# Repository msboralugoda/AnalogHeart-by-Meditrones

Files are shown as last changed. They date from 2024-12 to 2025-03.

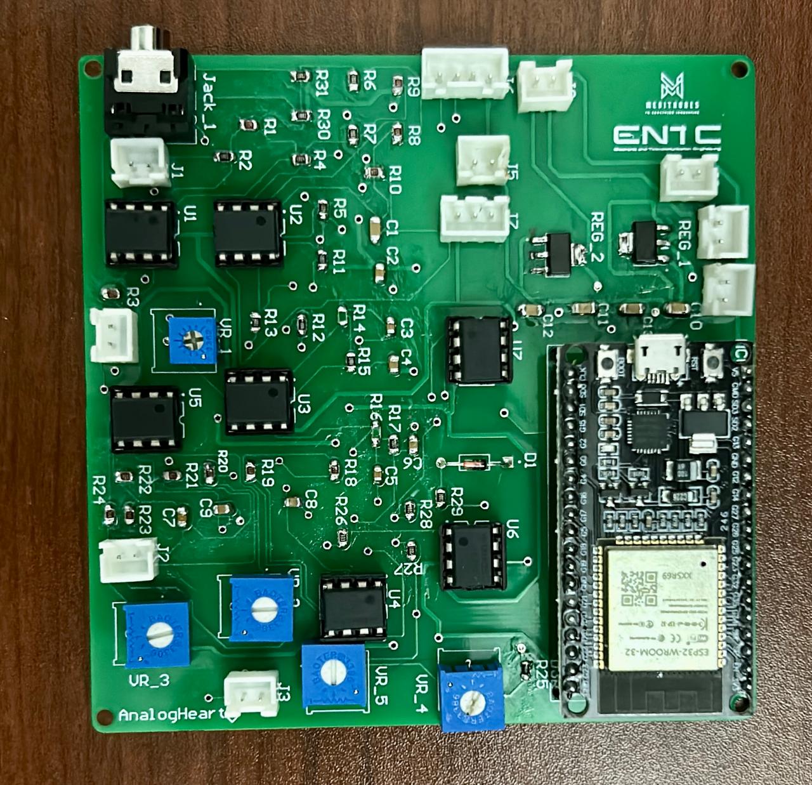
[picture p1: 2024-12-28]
Media/soldered pcb.jpg

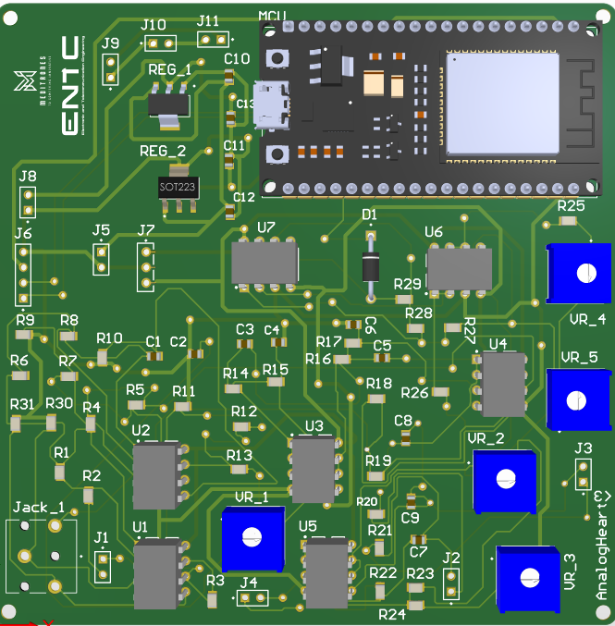
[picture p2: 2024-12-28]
Media/3D.png

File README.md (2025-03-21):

# AnalogHeart-by-Meditrones
This is the detailed project description of the ECG monitoring device built using analog electronics by the team Meditrones.
## Table of Contents
1. [Introduction](#introduction)
2. [Functionality](#functionality)
3. [Printed Circuit Board](#printed-circuit-board)
4. [Enclosure Design](#enclosure-design)
5. [Contributors](#contributors)

---

## Introduction
An electrocardiogram (ECG) is a widely used diagnostic tool for evaluating heart activity by detecting electrical signals through electrodes attached to the skin. These signals have amplitudes ranging from 0.001 mV to 100 mV and frequencies between 0.01 Hz and 180 Hz. However, amplifying and filtering these signals presents challenges due to their susceptibility to noise, power line interference, and other distortions.

Our project aims to address these challenges by designing an analog circuit that amplifies and filters ECG signals using basic electronic components such as resistors, capacitors, and operational amplifiers (OpAmps). The design incorporates multiple stages of signal conditioning, which are detailed below.

We simulated the design using LTSpice before implementation and used Altium Designer for PCB layout and SolidWorks for enclosure design.
Simulated Circuit

---

## Functionality
The AnalogHeart ECG Monitor includes the following features:
- **Real-time heart rate monitoring.**
- **User-friendly interface for operation.**
- **Accurate heart rate display with filtering.**
- **Adjustable settings for different scenarios.**
- **Data logging and export options.**
- **Detailed documentation for developers and users.**

### Signal Conditioning Stages
1. **Instrumentation Amplifier**
   - Amplifies small differential signals from the electrodes while rejecting common-mode noise.
   - Implemented using TL072CP OpAmps for high Common Mode Rejection Ratio (CMRR).
   - Adjustable gain using an external potentiometer.

2. **Right Leg Drive**
   - Reduces common-mode noise by injecting an inverted signal back into the body.
   - Built using a TL072CP OpAmp configured as an inverting buffer.

3. **Filter Stages**
   - **High Pass Filter**: Removes low-frequency noise and DC offset. First-order design with a cutoff at 0.15 Hz.
   - **Low Pass Filter**: Eliminates high-frequency noise using a fifth-order Bessel filter with a cutoff at 164 Hz.
   - **Notch Filter**: Suppresses power-line interference (50/60 Hz) with a Twin-T configuration and adjustable parameters.

4. **Power Circuit**
   - Dual supply (+12V and -12V) generated by TPS61040 boost converters for OpAmps.
   - 3.3V regulated output for ESP32 MCU using AMS117-3.3 regulator.
   - Rechargeable Li-Po battery support with a charging module for portability.

5. **Analog-to-Digital Conversion**
   - Captures conditioned ECG signals via ESP32's ADC input.
   - Includes level-shifting and scaling circuits to ensure signals fit within the 0-3.3V input range of the ESP32.

---

## Printed Circuit Board
The PCB was designed using Altium Designer and features:
- **Two-layer layout** for signal integrity and minimal interference.
- **Separate routing** for signal and power traces to reduce noise.
- **Compact design** with 0805 SMD components and IC bases for easy replacement.
- **Hand-soldered components** for prototyping and testing.
PCB

### PCB Highlights:
- **Power traces**: 25 mils for reliability.
- **Signal traces**: 15 mils to maintain integrity.
- **Isolated signal processing**, power, and ADC circuits.

---

## Enclosure Design
The enclosure was modeled using SolidWorks and designed for:
- **Protection and ventilation** to prevent overheating.
- **Removable top lid** for easy assembly and maintenance.
- **Battery holder and charging port** for portability.
- **Display mount and slots** for connectors, switches, and ventilation.
- **3D-printed construction** for rapid prototyping.


---

## Contributors
- **Aazir M.M.M** - Circuit design, enclosure design, and optimization.
- **Boralugoda M.S** - PCB design, documentation, and testing.
- **Liyanage D.L.B.B** - Circuit design, PCB assembly, and soldering.
- **Madusanka S.P.S** - Enclosure design and circuit testing.

---

For further details, visit the GitHub repository: [AnalogHeart by Meditrones](https://github.com/Banu-Liyanage/AnalogHeart-by-Meditrones)

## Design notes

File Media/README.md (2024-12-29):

This contain all the results and final design outputs of the project 
product_analog
This is the final device with the electrodes connected to the device.

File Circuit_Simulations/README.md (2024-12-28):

This contains the pathway to the circuit development and testing which includes the schematics and simulated results.
ECG_circuit_diagram
Above shown circuit is the main circuitry of the analog heart ecg monitoring device and it mainly consists of the Instrumentational Amplifier, High Pass Filter, Low Pass Filter and the Notch Filter

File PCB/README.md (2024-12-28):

This includes the PCB schematics of the analog project by team meditrones about the heart ECG monitoring device.

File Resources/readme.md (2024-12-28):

This contains some important resources we used while developing the circuit and for debugging purpoese as well.

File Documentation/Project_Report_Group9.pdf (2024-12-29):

Department of Electronic and Telecommunication Engineering

University of Moratuwa

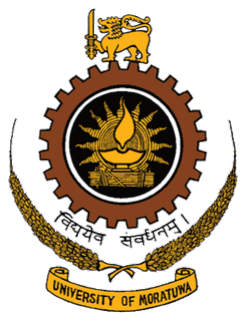
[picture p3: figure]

# AnalogHeart ECG Monitor

## Team Meditrones

## EN2091 - Laboratory Practice and Projects

Aazir.M.M.M - 220005R
Boralugoda.M.S - 220074B
Liyanage.D.L.B.B - 220362G Madusanka.S.P.S - 220374U

# Contents

1. | Introduction | | 2
2. | Functionality | | 3
2.1. | Instrumentation Amplifier | | | 3
2.2. | Right Leg Drive | | 3
2.3. | Filter Designing | | 3
2.4. | High Pass Filter | | 4
2.5. | Low Pass Filter | | 4
2.6. | Notch Filter | | 4
2.7. | Power Circuit | | 5
2.8. | Analog to Digital Conversion circuit | | 5
3. | Design Parameters | | 5
3.1. | Instrumentation Amplifier | | 5
3.2. | High Pass Filter | | 5
3.3. | Low Pass Filter | | 5
3.4. | Notch Filter | | 6
4. | PCB Design | | 6
5. | Enclosure Design | | 6
6. | Simulations and test Results | | 6
7. | Final Prototype | | 6
8. | Task Allocation | | 7
9. | Resources | | 7
10. References | | 7
11. Appendix | | 9
11.1. | PCB Layout from Altium Designer | | 9
11.2. Enclsoure Design using Solidworks | 10
11.3. Circuit Simulation and results | 12
11.4. Circuit Testing | 12

1

## Abstract

Our project was to create a circuitry that is capable of apprehending the ECG waveform and displaying it.This was achieved only using analog electronic components and they were used for several stages such as amplification, filtering and sampling purposes. Circuit is mainly made of instrumentation Amplifier , High Pass Filter,Low Pass Filter and a Notch Filter. This report also includes the PCB designs, simulations and the 3D Enclosure design made to meet the project requirements.

## 1. Introduction

An electrocardiogram (ECG) is a straightforward diagnostic method used to evaluate the electrical activity of the heart by identifying electrical impulses produced by electrodes affixed to the skin during each heartbeat. By using a feedback mechanism through the right leg, the voltage differential between the left and right arms is amplified. These voltages from the right arm, left arm, and right leg are measured via ECG leads. The voltage signal has a frequency between 0.01 Hz and 180 Hz and an amplitude between 0.001 mV and 100 mV (usually 1 mV).
The limited amplitude of the raw ECG signals and their vulnerability to distortion from a variety of causes, including noise, power line interference, radiofrequency interference, noise from electrode contact, stray capacitance and other biological factors makes it difficult to amplify and filter the ECG signal. Our circuit is composed of analog components like resistors, capacitors and OpAmps that is capable of amplifying and filtering out the ECG signal. Our circuit comprises of the following sections;
- Instrumentation Amplifier
- First Order Active High Pass Filter
- Fifth Order Active Low Pass Filter
- Notch Filter
- Right Leg Drive

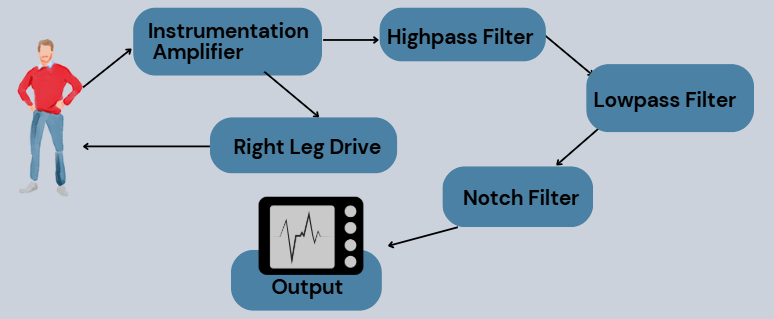
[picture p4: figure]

Figure 1: Functional block diagram

After simulating the circuit using LT-Spice we successfully implemented the prototype circuit and designed a PCB using Altium as well as an enclosure to meet the user demands using Solidworks.

2

## 2. Functionality

### 2.1. Instrumentation Ampli-

fier

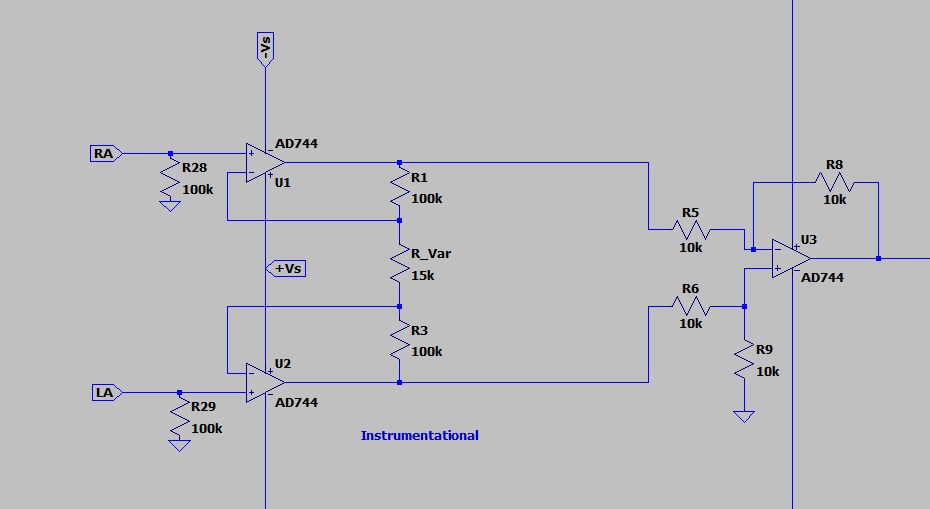
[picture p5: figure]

Figure 2: Instrumentation Amplifier

The main purpose of the instrumentation amplifier is to amplify the small electrical signals produced by the heart, which are typically in the millivolt range. It achieves this by amplifying the differential voltage between two electrodes while suppressing common-mode signals, such as interference from nearby power lines or artifacts from other biosignals.

In our instrumentation amplifier circuit design, it utilizes two
TL072CP | operational | amplifiers.
This IC was chosen for its moderate Common Mode Rejection Ratio (CMRR), with a value of 80 dB, making it sufficient for the amplification process. The circuit receives input through two ECG leads placed near Right and Left collarbones, and the gain can be adjusted using a variable resistor located centrally.

### 2.2. Right Leg Drive

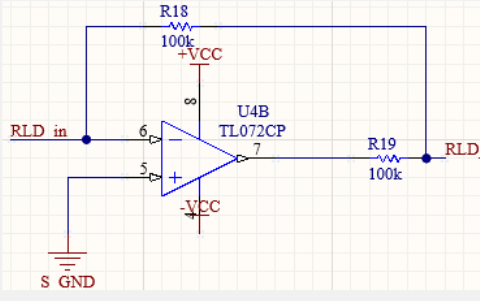
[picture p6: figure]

Figure 3: Right Leg Drive

The Right Leg Drive (RLD) circuit is used to reduce the common-mode noise between the two input electrodes. This is achieved by getting the original signal, inverting and amplifying it, then sending it back to the body through an electrode placed below the ribs. Here we use a single TL072CP IC and it acts as an inverting unity gain buffer.

### 2.3. Filter Designing

Selection of the proper cut off frequencies and the orders of the filters were few key things we had to consider when designing the circuit, by the literature review we did we came to a conclusion that the bandwidth of 160 Hz would be ideal and achievable from the available resources.The filter circuit consists of 1st Order High Pass Filter, 5th Low Pass Bessel Filter and a Twin-T Notch Filter.We decided to use TL072CP OpAmps for our filter circuits due to its better performance under noise.

3

### 2.4. High Pass Filter

Used to remove low-frequency noise and the DC offset from the ECG signal, such as baseline wander caused by patient movement or breathing. We decided to use a first order High Pass Filter because its performance met our expectations and we didn’t want to make the circuit bulky and costly by increasing order of the filter, the cut off frequency of the filter was 0.15 Hz.

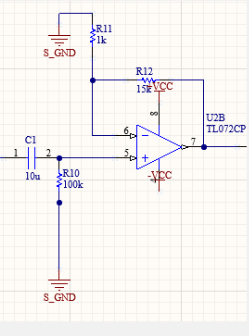
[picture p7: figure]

Figure 4: High Pass Filter

### 2.5. Low Pass Filter

Used to eliminate high-frequency noise from the ECG signal, such as muscle artifacts or electromagnetic interference. In our design we used a fifth order bessel filter by casacading two 2nd order sallen-key filters with a first order active filter.We chose the cut-off frequency to be 164 Hz. We were able to acheieve the expected output from the filter in this configuration.

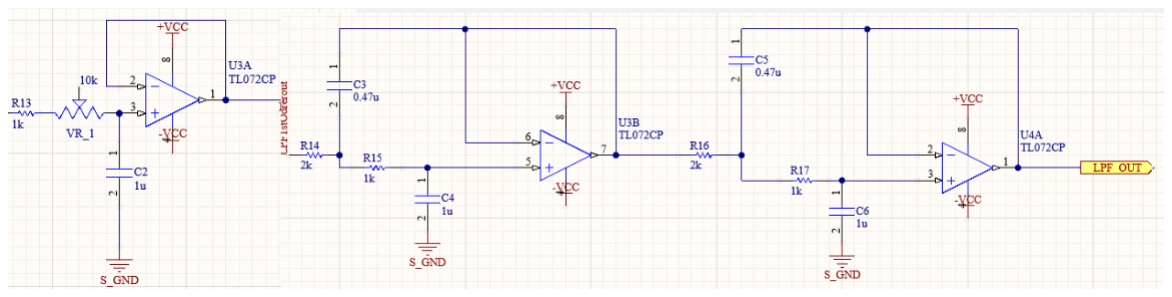
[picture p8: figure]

Figure 5: Low Pass Filter

### 2.6. Notch Filter

A Notch Filter was used mainly to overcome the power-line and other external interferences, this also improves the SNR of the ECG signal which preserves the P,Q,R,S,T complexes of the signal. Furthermore it is important to eliminate the power interference noise before feeding to the ADC as because it will sample the power noise as well which could complicate the signal processing. We used a Twin-T Notch Filter configuration and used external potentiometers to manually adjust the precise cut-off frequency and the steepness of the response.

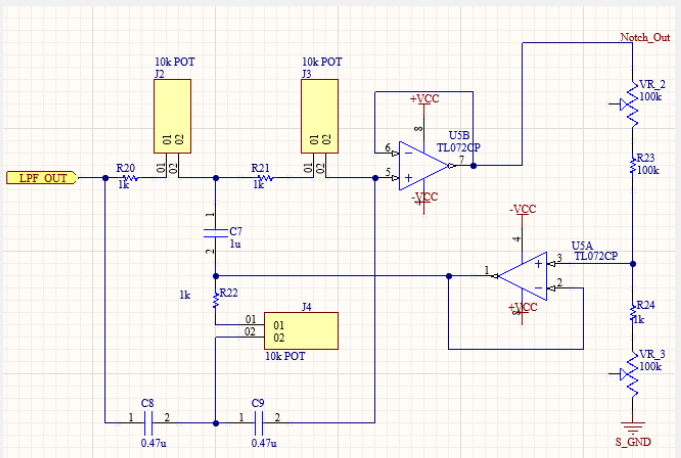
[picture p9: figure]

Figure 6: Twin-T Notch Filter

4

### 2.7. Power Circuit

The OpAmps TL072CP we are using need a dual supply as we decided to use a boost converter TPS61040 to produce +12V and -12V to power up the Opamps.Also we have used a DC-DC booster to power up the ESP-32 module after regulating through AMS117-3.3 regulator.
Furthermore we have proposed to use to a Lipo Battery to make the device portable and a charging module to make it user friendly for the user to recharge.

### 2.8. Analog to Digital Con-

version circuit

The signal is taken into the ESP32 Micro-controller through one of the chip’s inbuilt Analog to Digital conversion pins.
The constraint for ADC conversion is to provide signals only between 0-3.3V to the input pin.Since the notch filter output clearly exceeds this range we implemented a level shifting circuit to shift and scale down the output signal to the 0-3.3V range.

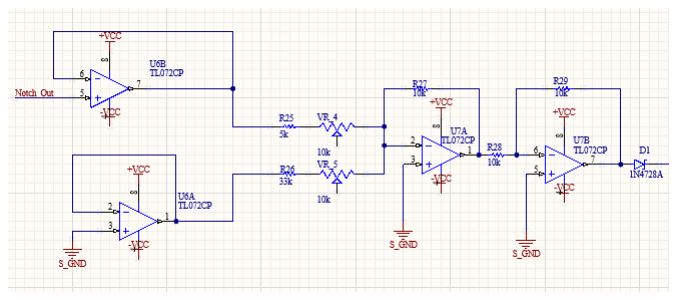
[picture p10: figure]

Figure 7: Scaling and Shifting Circuit

## 3. Design Parameters

### 3.1. Instrumentation Ampli-

fier

We have used an external potentiometer to vary the gain of the Instrumentaional Amplifier.

Furthermore | we | have | used
TL072CP OpAmps for this and used 0805 package SMD resistors to make the circuitry compact.

### 3.2. High Pass Filter

Included another gain from the active filter and the gain is around 17.25 where as the cut-off frequency is about 0.15Hz.

### 3.3. Low Pass Filter

We have used a fifth order Bessel filter with a cutoff frequency of 164.15Hz.

5

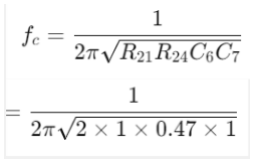
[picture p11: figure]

### 3.4. Notch Filter

The Notch filter has the Twin-T configuration and we have used external potentiometers to manually set the cutoff frequency and the steepness of the frequency response.

## 4. PCB Design

PCB design was made using Altium software which is a professional tool for building PCBs and used two layers to meet the quality standards. Power traces were routed using a trace width of 25mils to make sure the PCB is safe during power transmission and the signal traces were 15mils which is sufficient to keep the signal integrity.
The signal processing circuit was isolated from the power circuit and the ADC circuit to make sure there is minimum interference to the ECG signal from other components.SMD components were soldered by hand and placed IC bases for convenient replacement of OpAmps when required. All the layers and schematics are shown in the Appendix.

## 5. Enclosure Design

The enclosure is designed using Solidworks CAD software and this has several key components. It has a removable lid, a battery holder to place the batteries and remove them as required, it has a charging port to charge the batteries.Further it has a mount to place the display on the top lid and made required cuts for the ventilation inside the device. The 3D drawings are shown in the Appendix below.

## 6. Simulations and test Results

First we made the circuit in LTspice and confirmed the filers are working as expected and later we gave an ecg wave with noise and we were able to observe the filtered and amplified ECG from our simulated circuit. Later we developed the Prototype circuit and we were able to achieve the expected outcomes from the circuit we build. All the results are shown below in the Appendix.

## 7. Final Prototype

Shown below is the final product with the PCB mounted and components assembled inside the enclosure with the three electrodes.

Figure 8: Final Product

6

## 8. Task Allocation

Aazir.M.M.M- Circuit design, enclosure design, and circuit optimization.

Boralugoda.M.S- PCB | design,
documentation, | and circuit
testing.

Liyanage.D.L.B.B- Circuit design, PCB design, and soldering.

Madusanka.S.P.S- Enclosure design and circuit testing.

## 9. Resources

GitHub repository including all the schematic files, PCB and enclosure design files and code can be found here:
https://github.com/Banu-Liyanage/AnalogHeart-by-Meditrones (https://github.com/Banu-Liyanage/AnalogHeart-by-Meditrones)

## 10. References

Refer to the Texas Instruments guide on op-amp design [1]. For ECG sensor circuit designs, see the MedCrave article [2]. Detailed specifications for the TL072 op-amp are available in the datasheet [3].

7

# Bibliography

[1] T. Instruments, Op amps for everyone design guide, Accessed: 20-Dec-2024, 2002. [Online]. Available: https : / / www . ti . com / lit / an / sloa049d/sloa049d.pdf. (https://www.ti.com/lit/an/sloa049d/sloa049d.pdf)
[2] A. Idris, “Design of an ecg sensor circuitry for cardiovascular disease diagnosis,” International Journal of Bioengineering and Biomedical Science, 2018, Accessed: 20-Dec-2024. [Online]. Available: https://medcraveonline.com/IJBSBE/design-of-an-ecg-sensor-circuitry-for-cardiovasculardisease-diagnosis.html. (https://medcraveonline.com/IJBSBE/design-of-an-ecg-sensor-circuitry-for-cardiovascular-disease-diagnosis.html)
[3] T. Instruments, Tl072 low-noise jfet-input operational amplifier datasheet, Accessed: 20-Dec-2024, 2021. [Online]. Available: https://www.ti.com/lit/ds/symlink/tl072.pdf. (https://www.ti.com/lit/ds/symlink/tl072.pdf)

8

## 11. Appendix

### 11.1. PCB Layout from Altium Designer

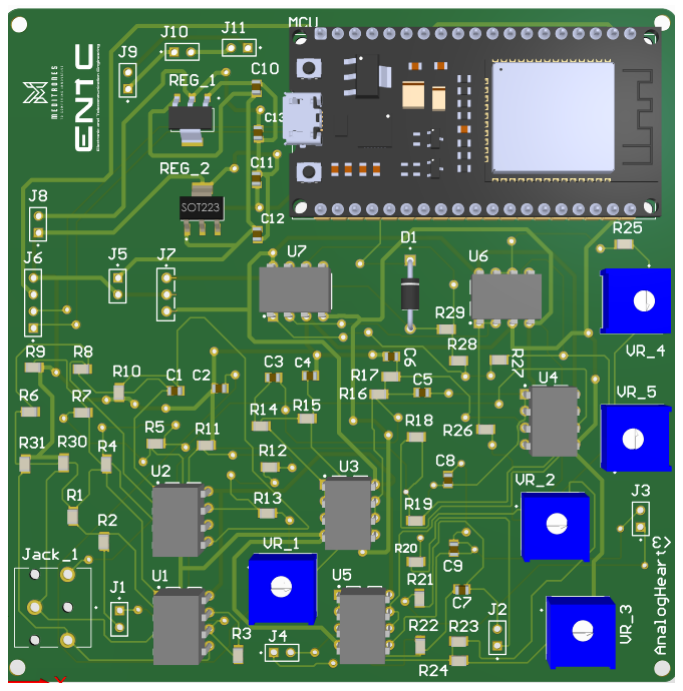
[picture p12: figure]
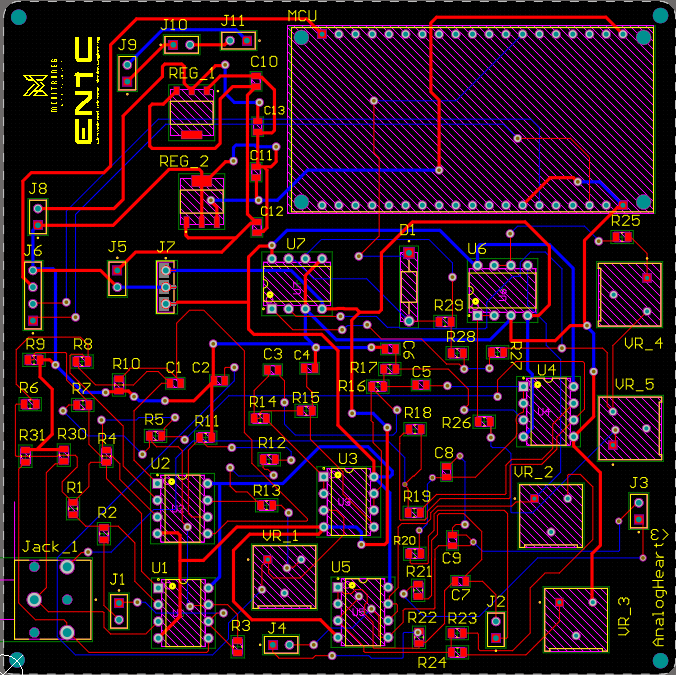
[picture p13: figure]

(a) All Layers of the PCB | (b) 3D View of the PCB

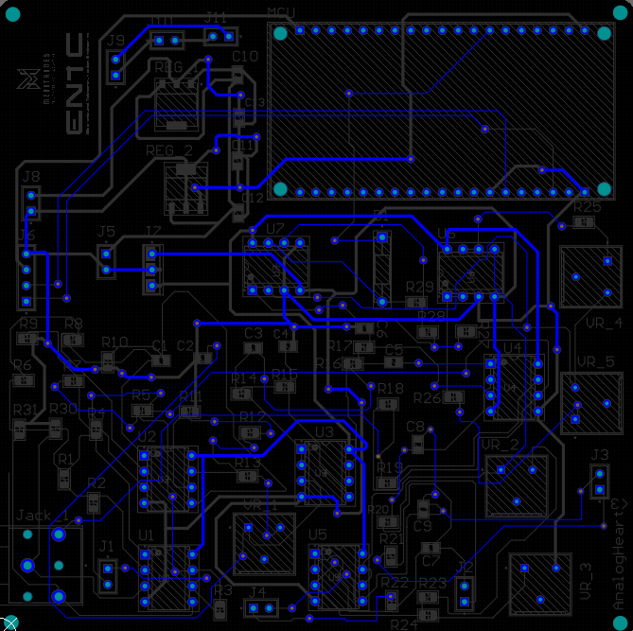
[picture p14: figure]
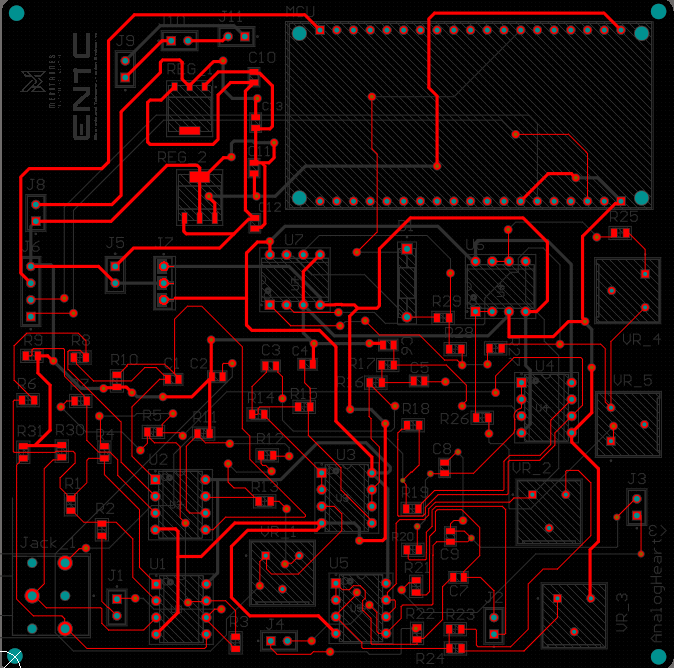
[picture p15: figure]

(c) Top Layer | (d) Bottom Layer

9

### 11.2. Enclsoure Design using Solidworks

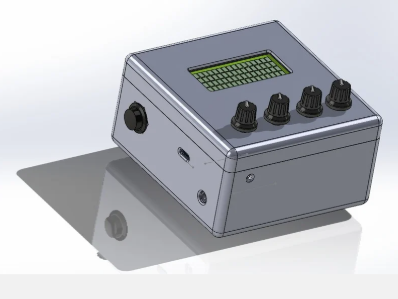
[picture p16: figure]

Figure 9: 3D view of the enclosure

10

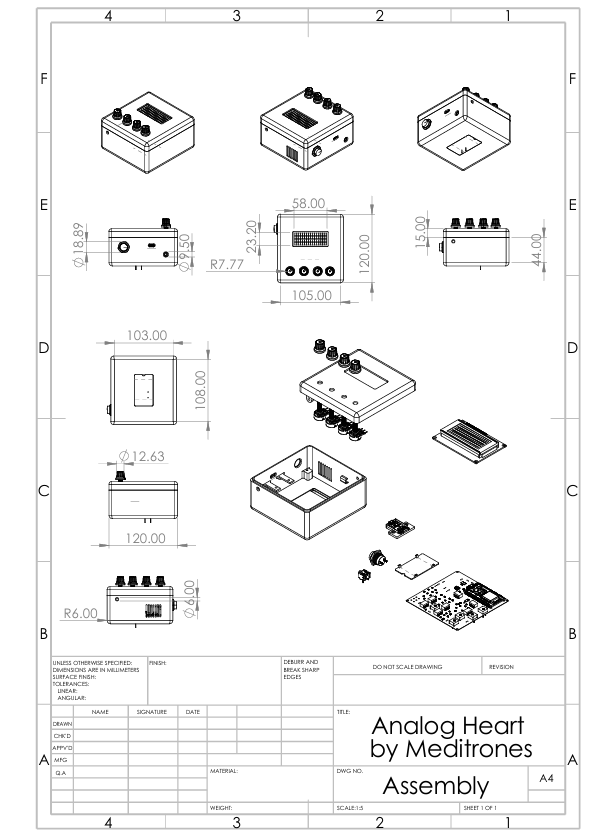
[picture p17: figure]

Figure 10: Drawings

11

### 11.3. Circuit Simulation and results

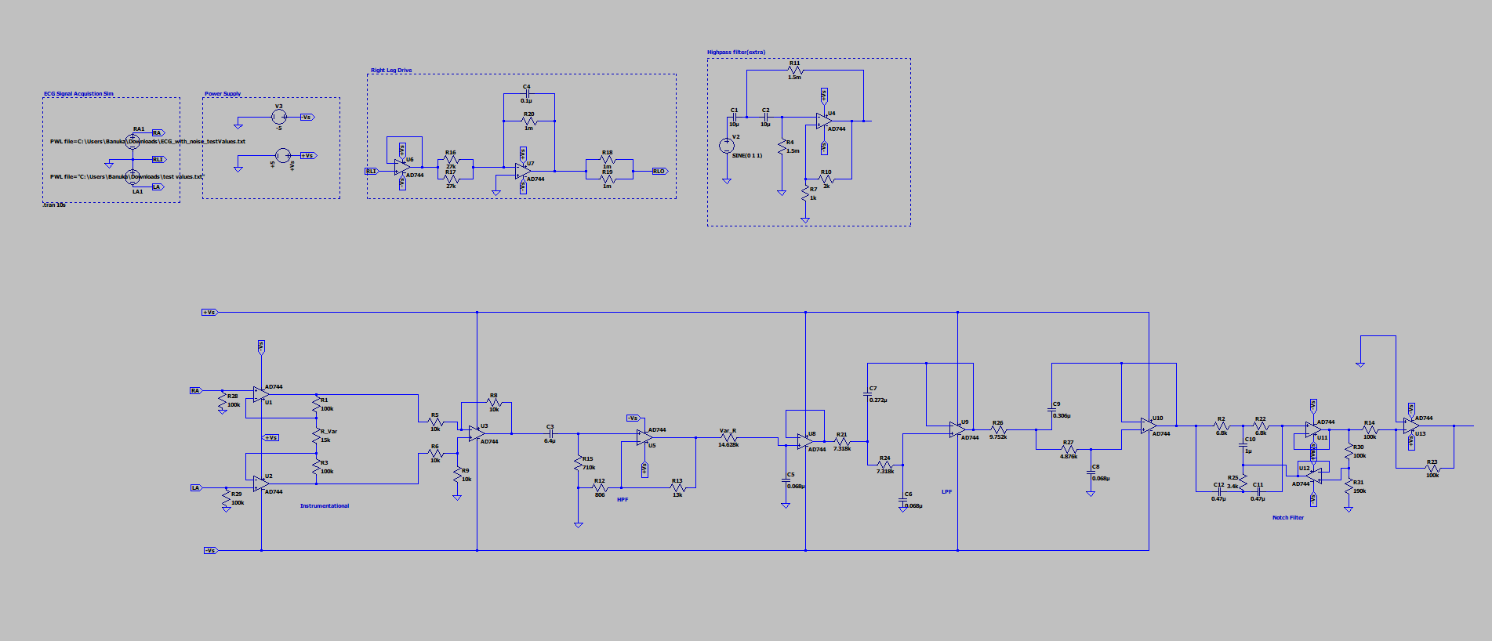
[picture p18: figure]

Figure 11: LTspice Schematic

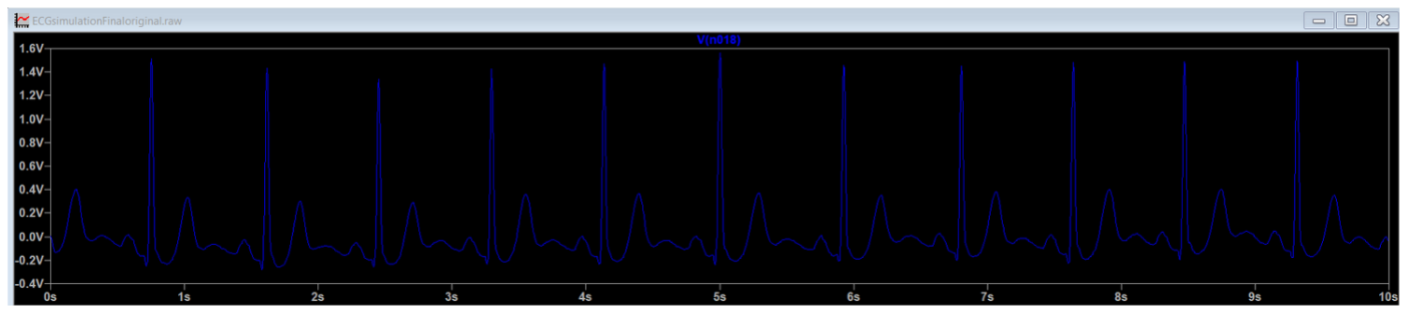
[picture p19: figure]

Figure 12: Simulation output from the LTSpice schematic

### 11.4. Circuit Testing

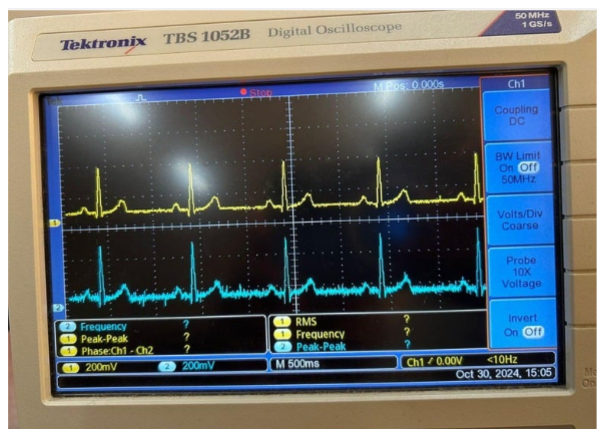
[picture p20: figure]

Figure 13: Output from the Prototype circuit

12

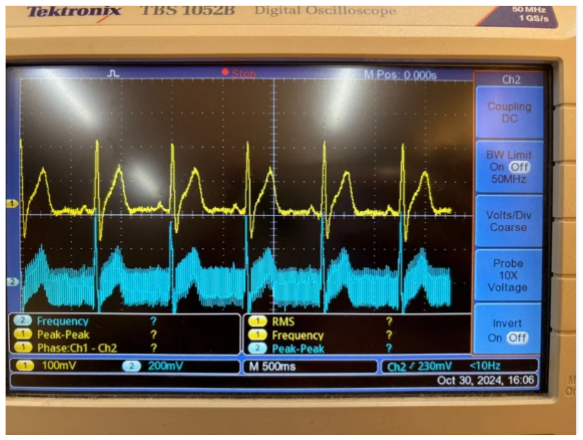
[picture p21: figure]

Figure 14: ECG wave from a live subject and the filtered wave, here the blue wave shows the input from the subject with noise and the yellow wave shows the final wave after amplifying and filtering

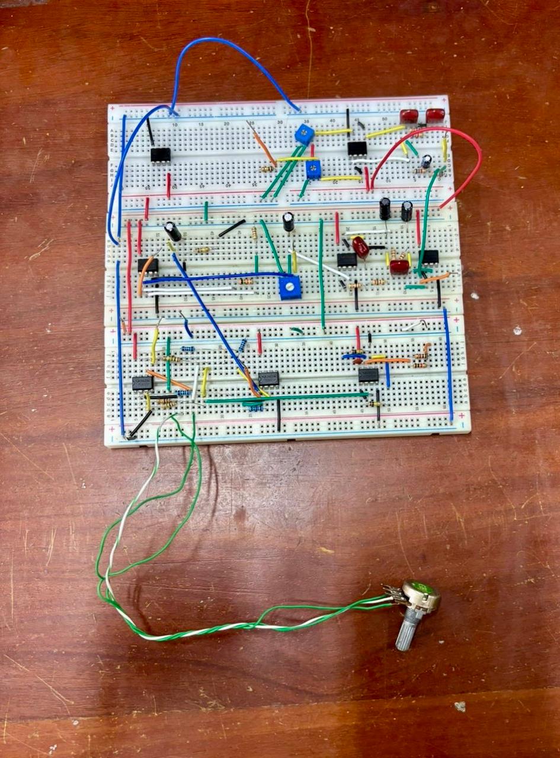
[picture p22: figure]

Figure 15: Initial Breadboard Circuit

13


Figure 16: Final Soldered PCB

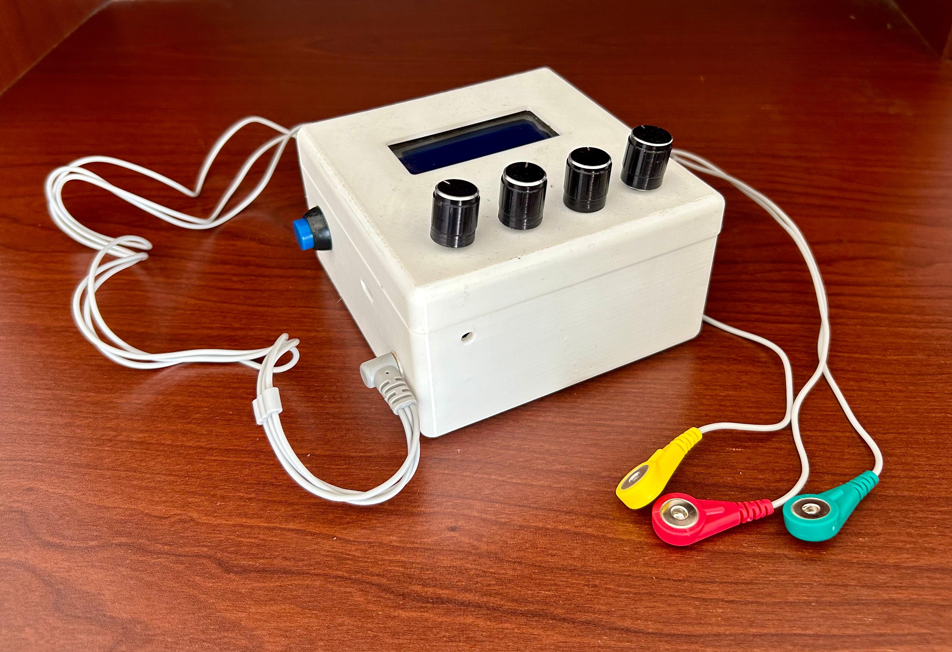
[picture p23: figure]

Figure 17: Final Device

14

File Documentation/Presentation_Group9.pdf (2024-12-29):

# ANALOG HEART

# HEART ECG MONITOR

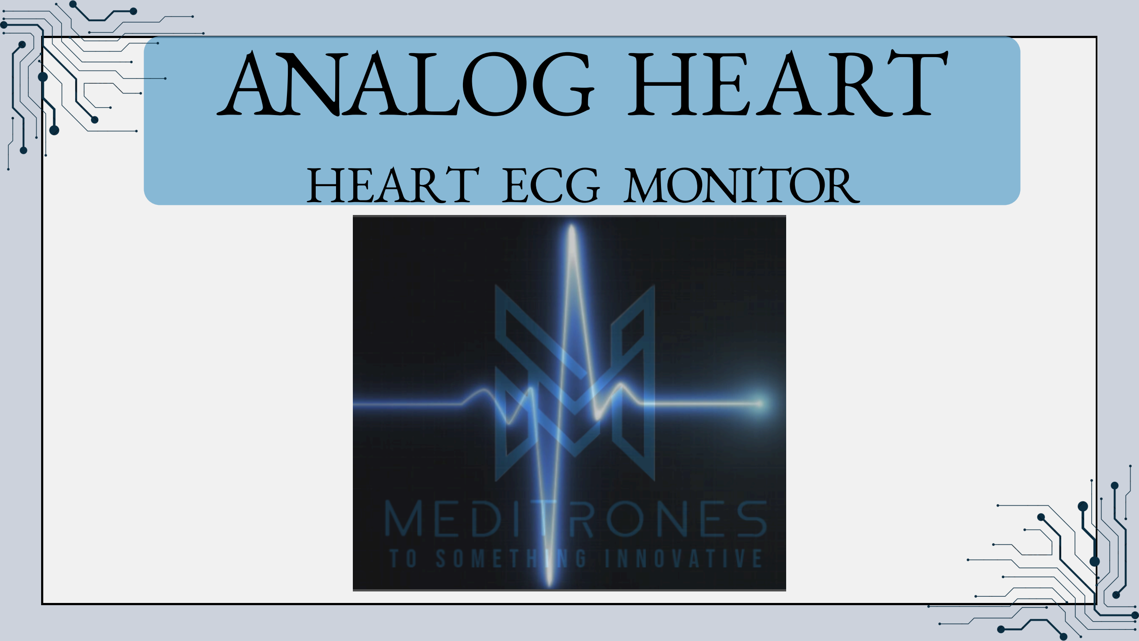
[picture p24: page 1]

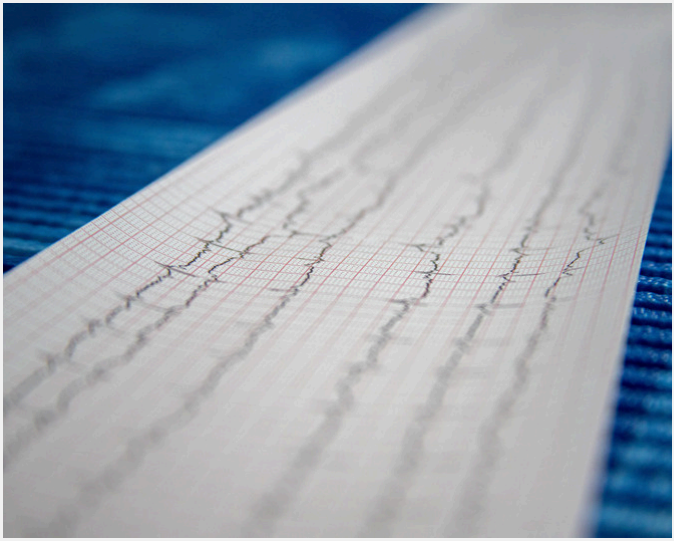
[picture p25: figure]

An ECG (Electrocardiogram) monitor measures the electrical activity of the heart to detect abnormalities in heart rhythm.

It records the heart'

s electrical signals using electrodes placed on the body.

The goal of our project is to design and build a high precision ECG monitor using analog components.

The device will amplify and filter the heart’s electrical signals to produce a readable ECG waveform.

# INTRODUCTION

# SYSTEMARCHITECTURE

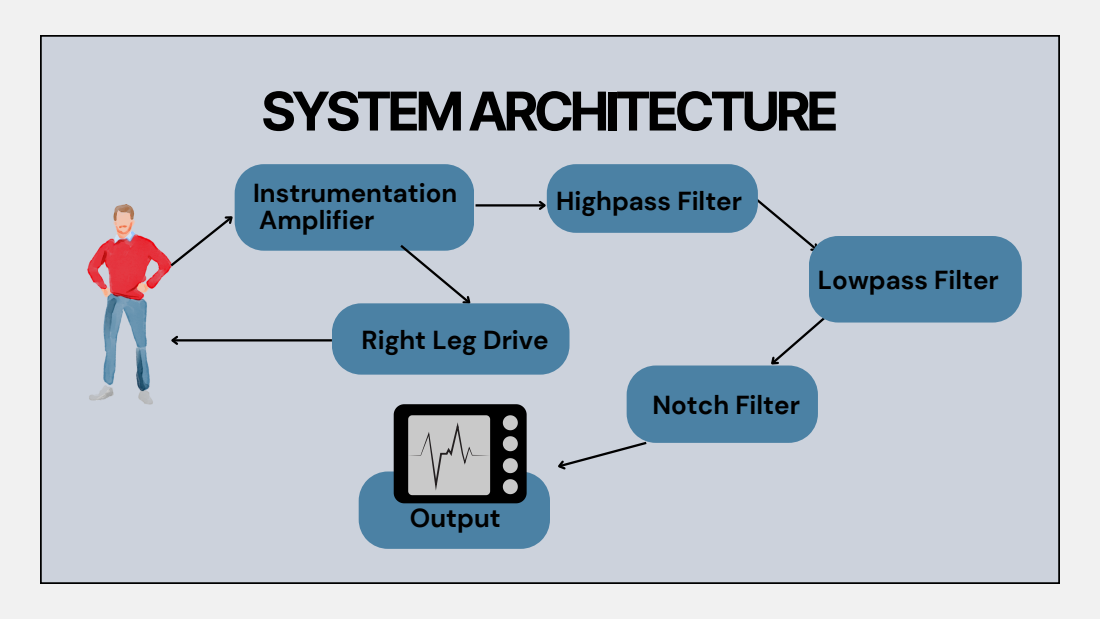
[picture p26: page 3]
Instrumentation Amplifier; Notch Filter; Highpass Filter; Lowpass Filter; Output

Right Leg Drive

Used to amplify the small differential voltage produced by the heart'


s electrical activity while rejecting common noise

Gain - | =

# INSTRUMENTATIONAMPLIFIER

# HIGHPASSFILTER


Used to remove low-frequency noise and the DC offset from the ECG signal, such as baseline wander caused by patient movement or breathing.
Gain - 17.25
Cutoff frequency - 0.15 Hz

Used to eliminate high-frequency noise from the ECG signal, such as muscle artifacts or electromagnetic interference.
Fifth order bessel filter is used.
Cutoff frequency - 164.15 Hz

# LOWPASSFILTERS


# LOWPASSFILTERS


1K

Used to eliminate power line interference, which typically occurs at 50 Hz

Twin-T Notch Filter with feedback is used.


Notch frequency - 50Hz

# NOTCHFILTER


Used to reduce common-mode interference (such as 50/60 Hz noise) by stabilizing the patient’s body potential.

# RIGHTLEGDRIVE


# POWER CIRCUIT

We are using a boost converter TPS61040 to produce +12V and -12V to power up the Opamps.

Also we have used a DC-DC booster to power up the ESP-32 module after regulating through ams117-3.3 regulator.

Furthermore we have proposed to use to a Lipo Battery to make the device portable and a charging module to make it user friendly for the user to recharge.

# SIMULATION


COMPONENTSELECTION-JUSTIFICATION (https://www.canva.com/design/DAGUGtDMFdo/nRQ5KC9qNzpNc9F0Ypxr8A/edit)


TL072 Op-Amp:
Low noise, high input impedance, and low power, good for ECG signals.
Dual op-amps reduce PCB space and cost.

SMD Resistors and Capacitors:
Compact size for portable design.
Better signal integrity and noise performance.

External Potentiometers:
Enables real-time filter adjustment for signal clarity.
Adjustable cutoff frequencies

COMPONENTSELECTION-JUSTIFICATION (https://www.canva.com/design/DAGUGtDMFdo/nRQ5KC9qNzpNc9F0Ypxr8A/edit)


LiPo Battery
Portability: Enables wearable, mobile ECG monitoring.
Battery-Powered Operation: Eliminates direct connection to mains power,
significantly reducing 50 Hz interference from power line noise.
High Energy Density: Provides long-lasting power in a small form factor.
Rechargeable: Reduces costs and environmental impact.
Stable Output: Ensures consistent performance for
sensitive circuits.
Safety: Built-in protection against overcharging and overheating.

# CIRCUITTESTING


Breadboard circuit - fluke

# CIRCUITTESTING


Breadboard circuit - human testing

# CIRCUITTESTING


PCB circuit - fluke

# CIRCUITTESTING


PCB circuit - human testing

# ENCLOSURE


# PCB


# TASKALLOCATION

## 220005R Aazir M.A.M. - Circuit design and enclosure design 220074B Boralugoda M.S. - PCB design and documentation 220362G Liyanage D.L.B.B. - Circuit testing and PCB design 220374U Madusanka S.P.S. - Enclosure design and Lab Testing


# THANK YOU!


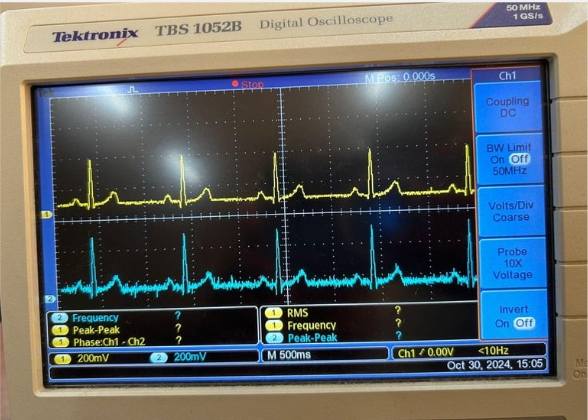
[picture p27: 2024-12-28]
Media/ECG_waveform_from_fluke.png

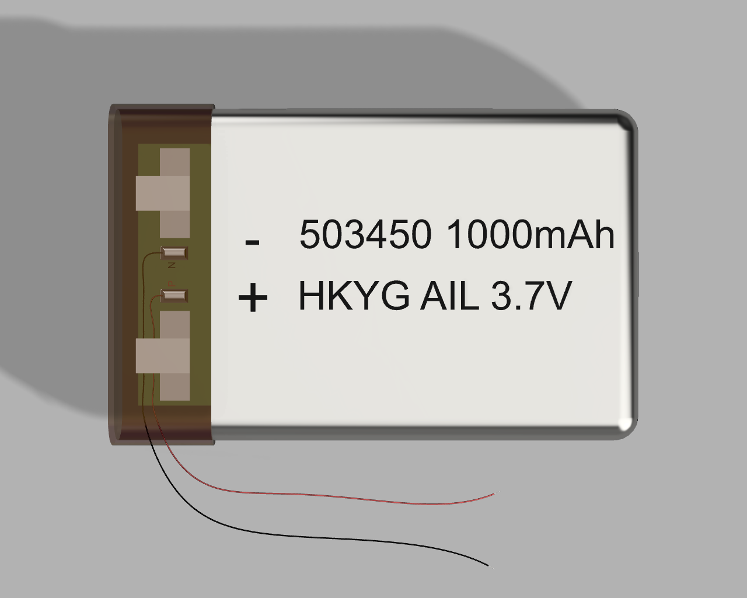
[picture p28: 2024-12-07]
Enclosure/bateria-lipo-3-7v-1000-ma-1.snapshot.1/Bateria LiPo 3.7V 1000mA 503450 v2.png

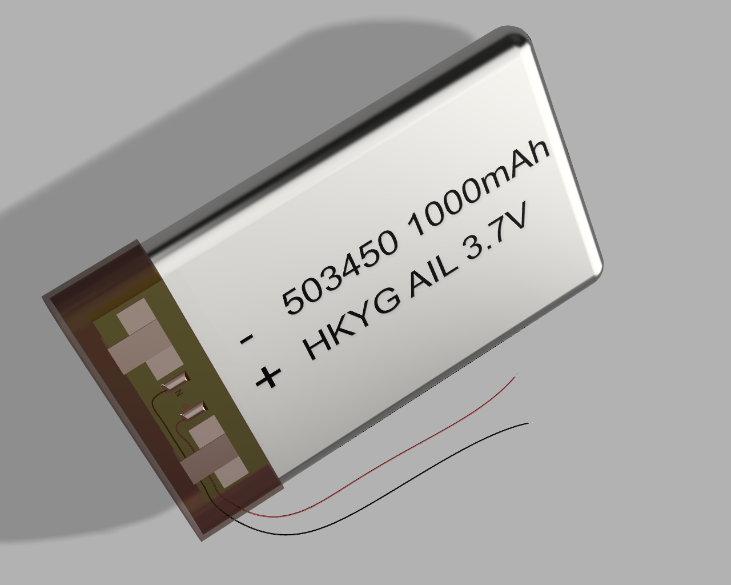
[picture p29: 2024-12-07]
Enclosure/bateria-lipo-3-7v-1000-ma-1.snapshot.1/Bateria LiPo 3.7V 1000mA 503450 v1.png

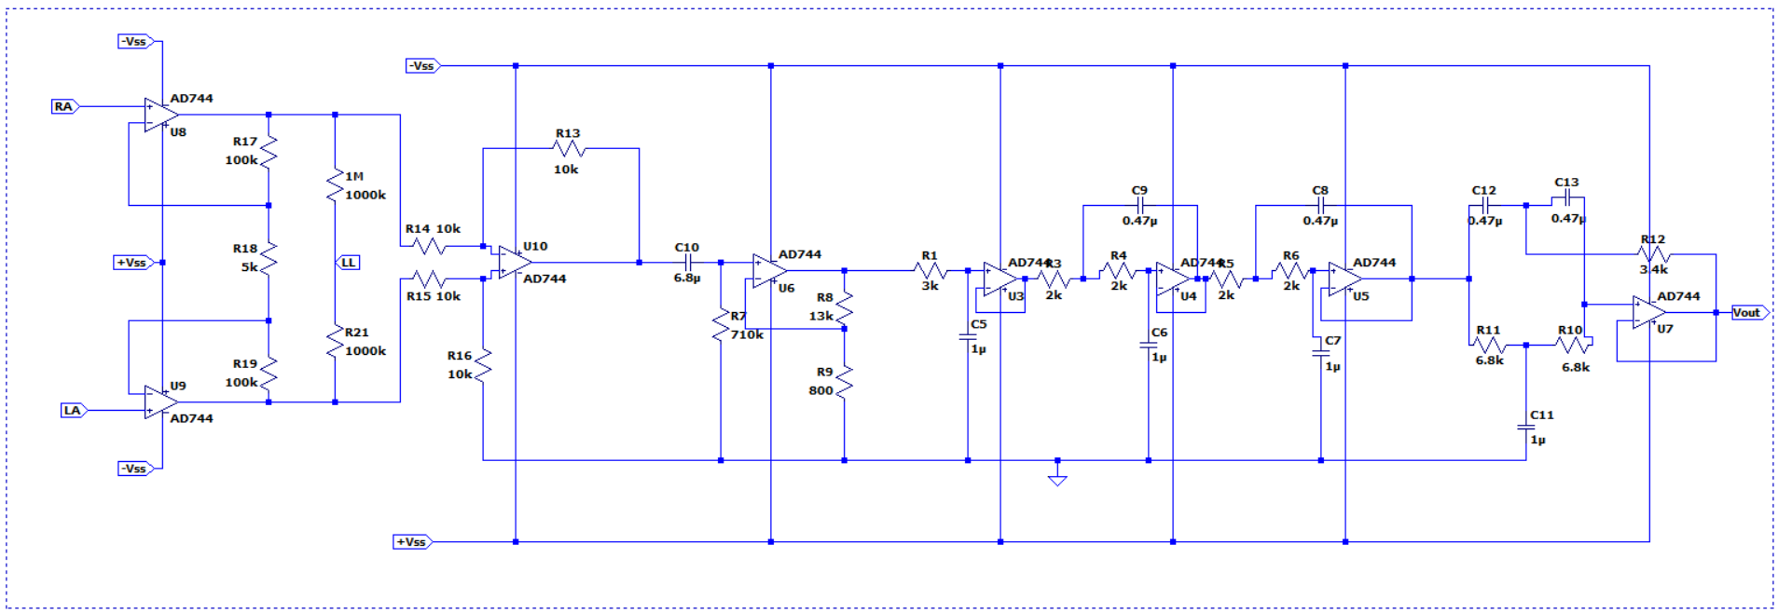
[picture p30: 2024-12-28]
Circuit_Simulations/ECG_circuit_diagram.png

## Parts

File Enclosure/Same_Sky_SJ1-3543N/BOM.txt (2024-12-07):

3DX_Same_Sky_Supplier: Same Sky
3DX_Same_Sky_Description: 3.5 mm Right-Angle Stereo Jack, 3 Pin PCB Mount, Non-Threaded
3DX_Same_Sky_Model Number: SJ1-3543N

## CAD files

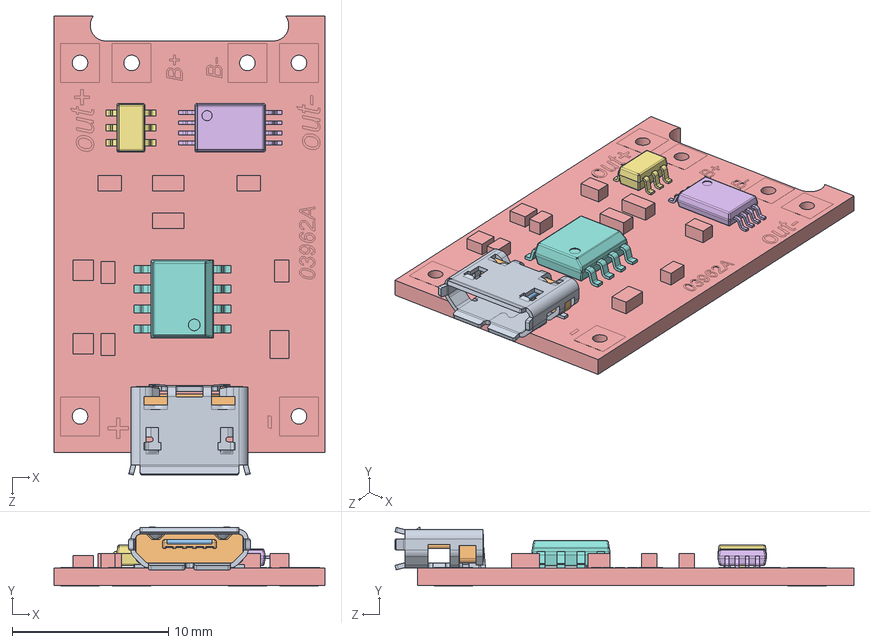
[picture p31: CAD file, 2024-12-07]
Enclosure/charge-liion-tp4056-03962a-1.snapshot.7/Плата ЗУ TP4056(03962A).SLDASM
17.3 x 3.76 x 29.4 mm
Копия shield^Копия micro_usb_connector_Плата ЗУ TP4056(03962A)
Копия socket_housing^Копия micro_usb_connector_Плата ЗУ TP4056(03962A)
Копия socket_plate^Копия micro_usb_connector_Плата ЗУ TP4056(03962A)
Копия terminal^Копия micro_usb_connector_Плата ЗУ TP4056(03962A) x 5
Деталь11^Плата ЗУ TP4056(03962A)
Копия MO-153AA^Плата ЗУ TP4056(03962A)
Копия SC-74^Плата ЗУ TP4056(03962A)
Копия MS-012AA^Плата ЗУ TP4056(03962A)

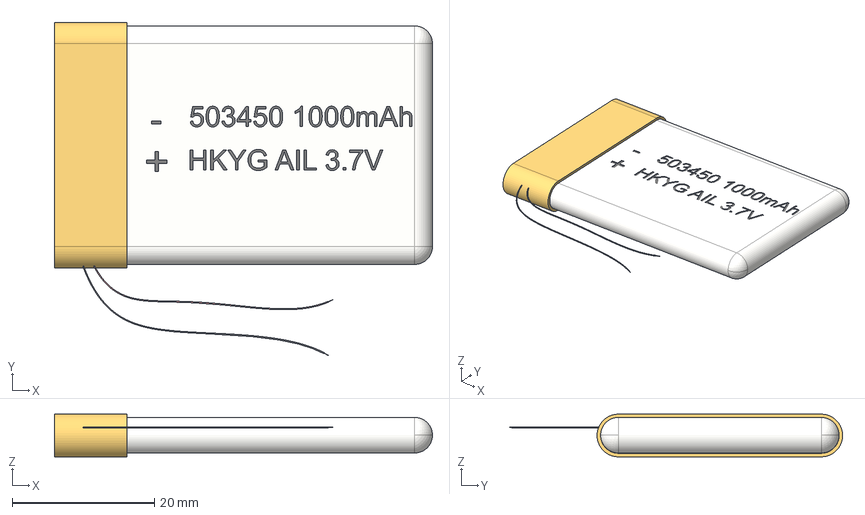
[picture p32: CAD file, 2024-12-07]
Enclosure/bateria-lipo-3-7v-1000-ma-1.snapshot.1/Bateria LiPo 3.7V 1000mA 503450 v23.step
53.1 x 46.8 x 6.00 mm

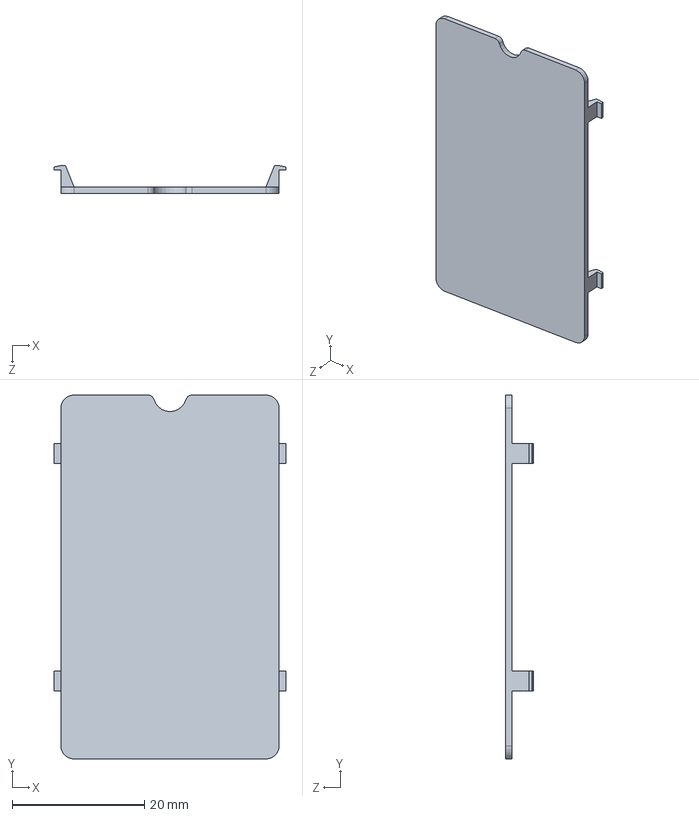
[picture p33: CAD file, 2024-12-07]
Enclosure/battery cover.SLDPRT
35.0 x 55.0 x 4.20 mm

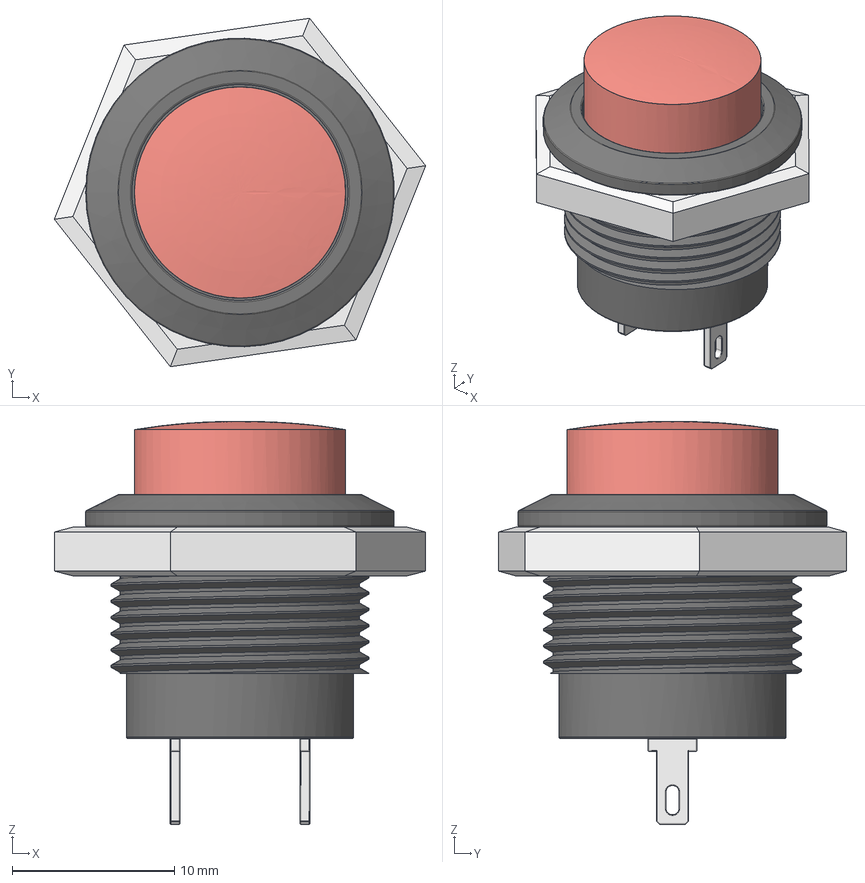
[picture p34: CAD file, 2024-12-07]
Enclosure/pushbutton-drucktaster-r13-507-1.snapshot.4/Drucktaster R13-507 rot v7.step
22.9 x 21.4 x 24.8 mm
Pol x 4
Taster rot
Mutter M16

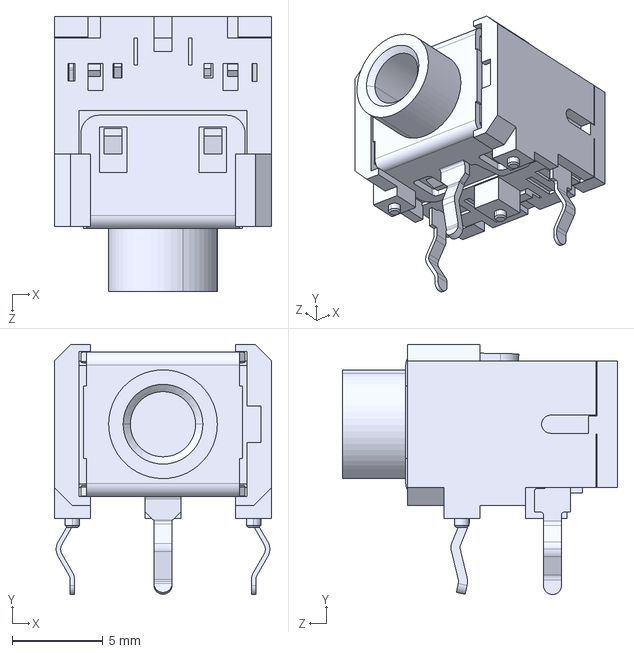
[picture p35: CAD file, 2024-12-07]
Enclosure/Same_Sky_SJ1-3543N/Same_Sky_SJ1-3543N.step
12.0 x 13.8 x 15.2 mm

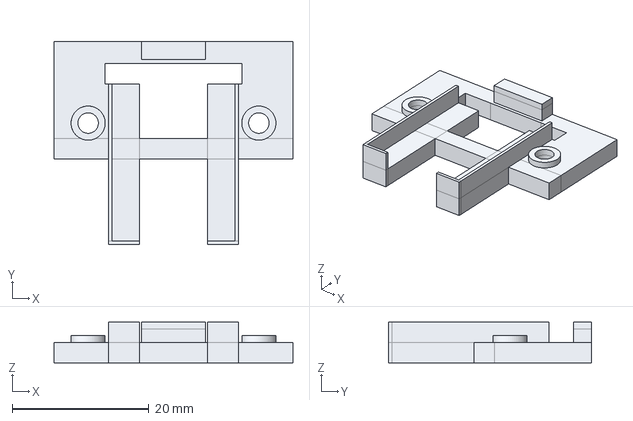
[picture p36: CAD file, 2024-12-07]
Enclosure/tp4056-bracket-holder-m2-1.snapshot.6/TP4056 Bracket.step
35.0 x 29.7 x 6.00 mm

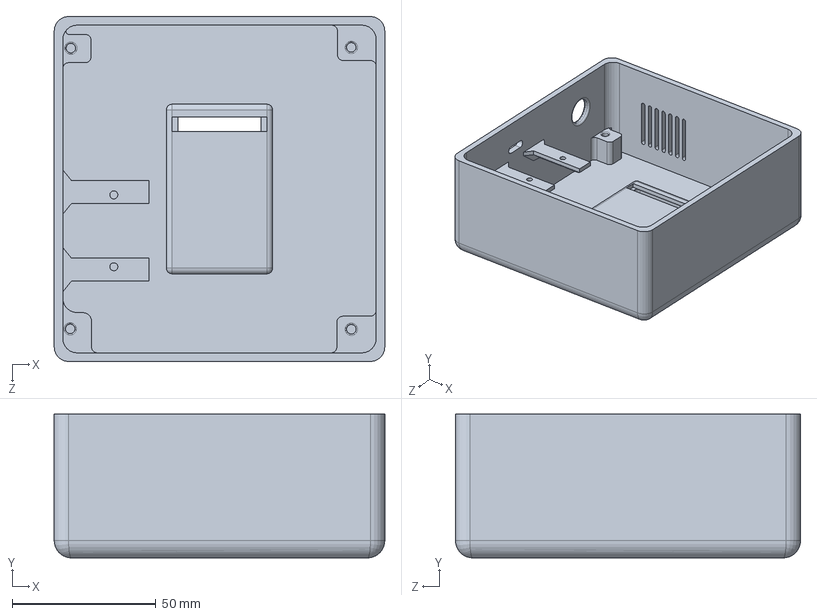
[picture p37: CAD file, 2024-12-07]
Enclosure/Base.SLDPRT
115.0 x 50.0 x 120.0 mm

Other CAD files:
Enclosure/pushbutton-drucktaster-r13-507-1.snapshot.4/Drucktaster R13-507 schwarz v8.step
Enclosure/pushbutton-drucktaster-r13-507-1.snapshot.4/Drucktaster R13-507 Metall v2.step
Enclosure/pushbutton-drucktaster-r13-507-1.snapshot.4/Drucktaster R13-507 Metall v2.iges
Enclosure/pushbutton-drucktaster-r13-507-1.snapshot.4/Drucktaster R13-507 rot v7.iges
Enclosure/pushbutton-drucktaster-r13-507-1.snapshot.4/Drucktaster R13-507 schwarz v8.iges

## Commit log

2024-12-28 Create PCB
    added folder to include pcb schematics
2024-12-28 added pcb schematics
    [AnalogHeart.PrjPcb, Sheet_3_AnalogHeart.SchDoc, analogheart_schem.SchDoc, sheet_2_AnalogHeart.SchDoc]
2024-12-28 Added simulations of the circuit
